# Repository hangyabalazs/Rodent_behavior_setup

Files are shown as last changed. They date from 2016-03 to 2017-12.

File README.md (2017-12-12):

# Rodent_behavior_setup
Useful parts for rodent behavior and electrophysiology experiments.

clamp.spk - Clamp for holding lickometer. Credit: Panna Hegedus

stage_arc.spk - Mouse stage for head-restrained behavior; half-tube design. Credit: Panna Hegedus

stage_rect.spk - Mouse stage for head-restrained behavior; rectangular design. Credit: Panna Hegedus

sound_attenuated_box - Sound attenuated enclosure for behavior experiments. Credit: Katalin Sviatko

Sound calibration - Bpod compatible Matlab code for calibrating sound pressure levels for pure tones and white noise for behavior. Credit: Nicola Solari

Sound_attenuation_BOM.docx - Bill of material for sound attenuation configurations. Credit: Nicola Solari

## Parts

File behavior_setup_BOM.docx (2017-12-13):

| Vendor/Cat.No. | Amnt | Price
Sound attenuated box
Steel mesh | Local shop | 1,5 m²
Hanno Protecto 50 - 20mm | Techfoam - Hanno Protecto 50 - 20mm | 1,5 m² | 16 EUR*1m²
Alfacoustic Pyramids 7cm | Muziker - 215894 | 1,5 m² | 15.90 EUR*1m²
Waterproof film | Local shop | 50x50 cm
Infrared light
DC12V SMD5050-300-IR InfraRed (850nm/940nm) Tri-Chip Flexible LED Strips 60LEDs 14.4W Per Meter (Length: 100cm; Color: - IR 850nm; Waterproof Type: IP65) | Ledlightsworld - HK-F5050IR30-X | 1 | 24.10 EUR
12v power supply | Local shop | 1
Video acquisition
Flea3 1.3 MP Mono USB3 Vision (Sony IMX035) | PointGrey - FL3-U3-13S2M-CS | 1 | 525 USD
USB 3.0, 3m, Type-A to Micro-B (Locking) Cable | PointGrey - ACC-01-2300 | 1 | 10 USD
Fujinon YV2.8×2.8SA-2, 2.8mm-8mm, 1/3", CS mount Lens | PointGrey - LENS-30F2-V80CS | 1 | 80 USD
Head-fixed setup
Aluminum Breadboard, 250 mm x 300 mm x 12.7 mm, M6 Taps | Thorlabs - MB2530/M | 1 | 116.1 EUR
Rubber Damping Feet, Set of 4 | Thorlabs - RDF1 | 1 | 4.59 EUR
12.7 mm XYZ Dovetail Translation Stage with Baseplate, M4 Taps | Thorlabs - DT12XYZ/M | 1 | 267,3 EUR
Ø12.7 mm Optical Post, SS, M4 Setscrew, M6 Tap, L = 75 mm | Thorlabs - TR75/M | 5/pack | 21,95 EUR
Mounting Base, 25 mm x 58 mm x 10 mm, 5-pack | Thorlabs - BA1S/M-P5 | 5/pack*2 | 21.06 EUR
"Ø12.7 mm Post Holder, Spring-Loaded Hex-Locking Thumbscrew, L=40 mm, 5-pack" | Thorlabs - PH40/M-P5 | 5/pack | 32.49 EUR
Rotating Clamp for Ø1/2" Posts, 360° Continuously Adjustable, 5 mm Hex | Thorlabs - SWC/M | 2 | 2*20.34 EUR
M4 Cap Screw and Hardware Kit | Thorlabs - HW-KIT1/M | 1 | 49.68 EUR
M6 Cap Screw and Hardware Kit | Thorlabs -HW-KIT2/M | 1 | 98.10 EUR
Adapter with Internal M4 x 0.7 Threads and External M6 x 1.0 Threaded Stud | Thorlabs - AS4M6M | 1 | 3.69 EUR
Fisherbrand Lab Jacks (Size: standard) | Fisher Scientific - S63081 | 1 | 125 USD
Sound delivery and calibration
Audio Adaptor Board for Teensy | Teensy - TEENSY3_AUDIO | 1 | 14.25 USD
Teensy USB Development Board | Teensy -TEENSY32 | 1 | 19.80 USD
Pins (header), 4 pins, 0.1 inch (2.54 mm) spacing, Double Insulator | Teensy - HEADER_14x1_D | 2 | 0.85 USD
SANDISK microSDHC 8GB Ultra Class10, 48Mb/s + Adapter (124065) | Local shop | 1
Adafruit Stereo 20W Class D Audio Amplifier - MAX9744 | Adafruit - MAX9744 | 1 | 19.95 USD
Digikey 8 Ohm Magnetic Speaker 3W 100Hz ~ 20kHz Top Rectangular 86dB | Digikey - 668-1447-ND | 2 | 2* 5.73 USD
3.5mm stereo jack to jack cable | Local shop | 1
Ethernet cable | Local shop | 1
EMM-6 Electret Measurement Microphone | Daytonaudio - EMM-6 | 1 | 79.99 USD
AudioBox iOne | PreSonus - AudioBox iOne | 1 | 159.95 USD
Male – Female three-pin XLR cable | Local shop | 1
USB B plug- USB A cables | Local shop | 1
Micro USB - USB A cables | Local shop | 1
12v power supply | Local shop | 1
Bpod
Bpod r0.5 beta | Sanworks - 1001 | 1 | 395 USD
Bpod port interface + valve | Sanworks - 1004 | 2 | 2*110USD
IR emitter | Digikey - 480-1969-ND | 1 | 2.26 USD
Phototransistor | Digikey - 480-1958-ND | 1 | 1.84 USD
White LED | Digikey - VAOL-3LWY4-ND | 1 | 0.65 USD
Micro USB - USB A cables | Local shop | 1
Ethernet cable | Local shop | 2
Micro USB – normal USB cables | Local shop | 1
Oscilloscope
PicoScope 2204A | Pico Technology | 1 | 139 USD

Item | File | Repository
Sound attenuated box | Sketchup | https://github.com/hangyabalazs/Rodent_behavior _setup
Lickport | Sketchup | https://github.com/hangyabalazs/Rodent_behavior _setup
Mouse platform | Sketchup | https://github.com/hangyabalazs/Rodent_behavior _setup
TeensyCalibration | Matlab | https://github.com/hangyabalazs/Rodent_behavior _setup

Nalgene™ 180 Clear Plastic PVC Metric Tubing - 1mm id (0.039 in) 2mm od (0.078 in) | Thermo Scientific - 8001-0102 | request quotation
Nalgene™ 180 Clear Plastic PVC Metric Tubing - 2mm id (0.078 in) 4mm od (0.039 in) | Thermo Scientific – 8001-0204 | request quotation
60ml syringe with Luer-Lok tips | BD Plastipak - 309653 | Contact local vendor
0.9mm diameter (20G) Syringe needles
Polyethylene tubing – 1.14mm id (0.045 in) 1.57mm od (0.062 in) | Warner Instruments – 64-0755/PE-160 | Contact local vendor

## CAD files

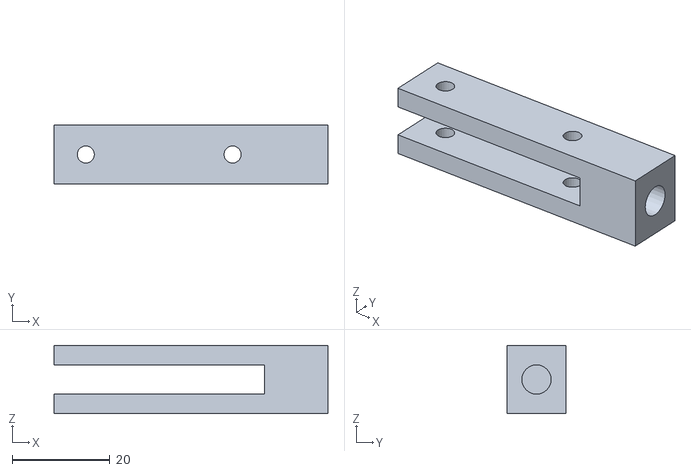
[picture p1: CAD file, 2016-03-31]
clamp_new2.stl
56.0 x 12.0 x 14.0

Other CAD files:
clamp.skp
clamp_new.skp
clamp_new2.skp
stage_arc.skp
stage_rect.skp
stage_rect_layers.skp

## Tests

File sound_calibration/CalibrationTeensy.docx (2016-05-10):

Sound calibration for rodent behaviour experiments

by Nicola Solari

Lendulet Laboratory for Systems Neuroscience

Institute of Experimental Medicine

Hungarian Academy of Sciences

hangyalab.koki.hu

Here we present a relatively cheap and simple setup that will allow you to play pure tones from 1kHz to 21kHz with the same dB SPL level, overcoming the standard-speakers’ innate lack of precise equalization.

Two things should be kept in mind: firstly, this protocol is designed for an experimental setup dedicated to head-fixed rodents; secondly, it does not deal with sounds above 21kHz: indeed common commercially available speakers cannot efficiently handle frequencies above this boundary, neither can affordable calibrated microphones.

Materials

Bpod

https://sanworks.io/shop/viewproduct?productID=1001

EMM-6 Electret Measurement Microphone

http://www.daytonaudio.com/index.php/emm-6-electret-measurement-microphone.html

AudioBox iOne

http://www.presonus.com/products/AudioBox-iOne/features

TrueRTA Real Time Spectrum Analyser

https://www.trueaudio.com/rta_down.htm

LogitechSpeakers Z150

http://www.logitech.com/en-us/product/multimedia-speakers-z150

Teensy 3.2 and Audio Adaptor Board

https://www.pjrc.com/teensy/teensy31.html

https://www.pjrc.com/store/teensy3_audio.html

SD Card 8GB class 10

https://www.sandisk.com/home/memory-cardsCalibrationTeensy function

CalibrationTeensyHB.m

Setup

As almost all calibrated microphones, the EMM-6 needs a phantom power source to work: we adopted the iOne board, which is in turn connected to the computer. This microphone works with 48V, so the 48V button on the front of iOne case should be switched. Set the input gain for the mic just one click below the maximum. Place the tip of the microphone where the head of the animal will be positioned.

On the TrueRTA interface, select iOne as the input source in the Audio I/O options, and click on the SPL button to visualise dB SPL, because as default it shows dBu.

Connect the assembled Teensy device to your Bpod following the instructions on the wiki (https://sites.google.com/site/bpoddocumentation/bpod-user-guide/function-reference/teensysoundserver). Plug the speakers to Teensy and place them where they will be situated during your experiment. For a precise and optimal performance of the membranes, turn their knob to the maximum volume.

Save the CalibrationTeensy Matlab function in the Bpod Protocols directory in a homonymous folder.

Procedure

Launch the function from the Bpod interface selecting the CalibrationTeensy protocol. This protocol will create calibrated pure tones from 1kHz to 21kHz and store them as 2 second long wav files in your Teensy SD card. In the beginning you will be asked to choose the frequency resolution for calibration in this range: 1kHz, 0.5kHz or 0.25kHz. The first option will generate one tracks for every 1000Hz from 1kHz to 21kHz (1kHz, 2kHz, 3kHz, 4kHz etc..), the second tracks for every 500Hz from 1kHz to 21kHz (1kHz, 1,5kHz, 2kHz, 2,5kHz etc..), the third tracks for every 250Hz from 1kHz to 21kHz (1kHz, 1,25kHz, 1,5kHz, 1,75kHz etc..). So, according to your decision, you will end up with 21, 41 or 81 audio files coding pure sinewave pitch.

Therefore, the program will create and write on the SD Card a first set of sinewaves with the same arbitrary amplitude (0.3). Once the upload is complete, the True RTA interface and an excel file named Calibration will be opened: use the former to observe the sound volume (dB SPL) generated at each pitch and enter it in the latter, below the corresponding kHz value marked in the first row. The tones will be produced using the Bpod interface: LED2 will light up, and after one second a tone is played: to move to the next one use the poke button 3, to repeat it the poke button 1. The frequencies will be played progressively, i.e. from the lowest to the highest.

After saving and closing the xlsx file, you will have to choose the target dB SPL for your tones. Sine amplitudes will be adjusted accordingly, and a new set of wav files will be created. Next you have to repeat reading the SPL values for each pitch and update the Calibration.xlsx files as instructed. Amplitudes will be adjusted once more, and you will have to check the final result. Generally this is good enough for the frequencies to be played at the same SPL.

Subsequently, you will have the option to continue and create a white noise sound, or to stop the protocol. In the former case a white noise wav file will be loaded and played with the same Bpod interface procedure. You should read the dB SPL values for each 1kHz, 2kHz, 5kHz, 10kHz and 20kHz octave and report them below the newly appeared headers in the Calibration Excel file. Again, save and close the xlsx and wait for the new calibration: the new white noise track will then be played. However, don’t expect the sound to have an equal volume on all the frequencies (as the definition of white noise states): due to software and hardware limitations that’s what we could achieve at the moment. Nonetheless, the dB SPL distribution is acceptable for most purposes.

Additional Notes

It’s important to note that, whenever speakers or mouse locations are changed, speakers should be re-calibrated.

Whenever the 48V button is pressed, the input gain knob should be previously positioned on the minimum level: this will ensure a longer life to the microphone.

Bpod, Teensy 3.2 and Audio Adaptor Board are the only pieces of hardware that are essential to run this program: all other components are substitutable with other analogous alternatives.

If you already possess a software capable of reporting dB SPL levels, you don’t need TrueRTA: simply modify the path in the code.

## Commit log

2015-10-07 Useful parts for rodent behavior and electrophysiology experiments.
    [clamp.skp, stage_arc.skp, stage_rect.skp]
2015-10-27 Less sturdy clamp.
    [clamp_new.skp, stage_rect_layers.skp]
2015-12-10 Three versions of acoustic isolation (NS)
    Sound attenuation was tested for the behavior box with three versions of
    sound isolating material. For the first setup, a sand board was combined
    with pyramid foam. In the other two setups, the sand boards were
    replaced by different sound attenuating foams. These provided
    approximately equal sound attenuation quality, while they were easier to
    work with and resulted in lighter boxes.
    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
2016-03-31 Update of the lick port clamp
    More stable version. By Panna Hegedus
    [clamp_new2.skp, clamp_new2.stl]
2016-05-10 Sound calibration
    Sound calibration for Teensy sound server. A doc with description and a
    Matlab .m file is uploaded. By Nicola Solari.
2017-12-12 BOM for sound attenuation
    bill of materials for sound attenuation configurations
2017-12-12 new sound attenuated box
    new design file for enclosure
2017-12-13 Delete TeensyCalibration.m
    obsolete
2017-12-13 new TeensyCalibration.m file
    with improved documentation
2017-12-13 Bill of materials for behavior setup.
    Sound attenuated box, infrared light, video, head-fixed setup, sound calibration, Bpod, oscilloscope.
